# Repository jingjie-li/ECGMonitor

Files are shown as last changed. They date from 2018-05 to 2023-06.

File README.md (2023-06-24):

# Overview
This is a ECG/SPO2 Monitor Project. We mainly used TI's (Texas Instrument) [ADS1293](http://www.ti.com/product/ads1293)/[AFE4400](http://www.ti.com/product/AFE4400/description) analog front-end IC to acquire physiology data form human body, and used TI's [MSP430F149 MCU](http://www.ti.com/product/MSP430F149/description) to control these Chips, and send the data to our Android Smartphone App via TI's Bluetooth IC [CC2540](http://www.ti.com/product/CC2540/description). In our smartphone App, we can display ECG/PPG wavefore, compute & display SPO2,Heart Rate, and Heart Rate Variability(HRV), and control the hardware to running on different acquision mode (such as 3-Leads or 5-Leads mode).

To do so, we disigned and made a custome PCB using Autodesk EAGLE, did embedded system programing for MSP430 using IAR IDE, and some stuff about smartphone APP. We also had a 3D printed case for our circuit.

The major advantages of our system, is our outstanding power consumption performance. Our hardware only took about 300mW Power for Li-ion battery (about ~180mW for bluetooth). Also, our PCB is super portable, size less than 10-by-10cm.

We Shared the majority of our code and design files. Including MSP430 program, PCB layout, 3D printing models, and some APP code.

We do these stuff is for a [National BME(Biomedical Engineering) Competition for College Students](http://bmedesign.medmeeting.org/cn) in ShenZhen, China.

__On Aug 28, 2018: We just won the FIRST PRIZE in [National BME(Biomedical Engineering) Competition for College Students](http://bmedesign.medmeeting.org/cn) in ShenZhen, China. Which is the HIGHEST AWARD.__

Our Trophy and Certification

__Fig 1 Our First Prize Trophy and Certification__

# Quick access of our sub-modules
+ [Main MCU Controling Code](https://github.com/celelion/ECGMonitor/blob/master/MSP430/AFE%26ADS_inter/main.c)
+ [PCB Layout](https://github.com/celelion/ECGMonitor/tree/master/PCB)
+ [APP](https://github.com/celelion/ECGMonitor/tree/master/APP_Design)
+ [3D Printed PCB Case](https://github.com/celelion/ECGMonitor/tree/master/Case)
+ [Processing Tools for Computer Debugging](https://github.com/celelion/ECGMonitor/tree/master/Analog_Front/EEGPPGdataRecTest)
+ [Arduino DUE based IC chip(ADS1293/AFE4400) SPI interface verification code](https://github.com/celelion/ECGMonitor/tree/master/Analog_Front/Arduino-TestFirmware)

# Features
## Characteristics and Technical Indexes
### ECG

+ Differential Input Voltage Range: -400 mV ~ +400 mV
+ Common-Mode Rejection Ratio(CMRR): >100 dB
+ Differential Input Resistance: 500 MΩ
+ Sampling Rate: 150 Hz

### Oximeter
+ Sampling Rate: 50 Hz

### Power Consumption
| Overall Power | Bluetooth | ADS-ECG Module | AFE-Oximeter Module | MSP430-MCU Module |
| ------ | ------ | ------ | ------ | ------ |
| 291.1103 mW | 177.7327 mW | 3.1984 mW | 93.0931 mW | 17.0861 mW |

# Development Team
+ Jingjie Li (jingjie.li.21@ucl.ac.uk) - Hardware, PCB Layout, Part of MSP430 Programming, Debugging tools using Processing IDE, 3D modeling for the case
+ Jinming Li (lijinmingli@foxmail.com) - MSP430 Programming, Testing
+ Haoyi Tao - Android APP Programming

We are all class of 2019 BME undergraduate student from Xi'an Jiaotong University

# Hardware (By Jingjie Li)

Hardware

__Fig 2 The PCB layout of ECG/SPO2 Monitor Hardware__

We had a MainBoard, which contains mainly 5 modules, which is 
+ LDO Module for power supply; 
+ ADS Module for ECG; 
+ AFE Module for SPO2; 
+ MCU Module for controlling ;
+ Debugging module, for downloading program(BSL), Serial-USB conversion for a convenient debuging on PC using Processing IDE.

Parts

__Fig 3 Different parts and modules on our Main PCB__

## Power Tree

We used 4.8V Li-ion Battery or 5V USB to powering the whole system. 5V/4.8V is directly feed to USB chip CH340, and the Bluetooth Module. A TI LM1117 LDO chip proveide 3.3V power to ADS1293 ECG Module, and MSP430 MCU Module. 

PowerTree

__Fig 4 The Power Tree of our MainPCB__

Powering AFE4400 is a little bit more complicated, to give AFE4400 IC a much more stable voltage supply, we used a Ultra-Low-Noise, High-PSRR [TI TPS7A49](http://www.ti.com/product/TPS7A49/description) chip to provide 3V power for the AFE4400's digital supply (DIG SUP) pins. Then, we used a Low Noise 'Ceramic Stable' LDO [TI LP3878](http://www.ti.com/product/LP3878-ADJ/samplebuy) to provide 3.7v power for AFE4400 LED drive power supply pins (LED DRV). Using two chips, provided us a better isolation in AFE4400, which could minimize the voltage fluctuation interfere from ADS, MCU or AFE LED DRV parts.

## Connectors

For a common use, we choosed standard connectors and cables in our hardware design.

Hardware connection

__Fig 5 Hardware Connectors__

For example, for ECG, we used Mindray Standard 6-Pins, 5-Leads ECG cables and connectors; For SPO2, we used the standrad DB9 SPO2 Probe connector. So, it will be easy for our users to find new replcement when old probe is damaged.

## Signal Flow in our PCB

SignalFlow

__Fig 6 Signal Flow in our PCB__

In our hardware, we used MSP430 MCU to drive the SPI Bus (as a master device) to configrate ECG and SPO2 Chips (Write data on specific address), and read digital data form each chip.

The MSP430 MCU then compress, encode the sampled data to a long int, and send to the Bluetooth module (To smartphone APP) or a serial-USB debug module via UART.

MSP430 MCU also controled several indicator LED, which we could visulize the sampling rhythm (By flashing of the ADS/AFE LED). LEDs can also provided alarms such as ECG Lead off, SPO2 Cable off for us.

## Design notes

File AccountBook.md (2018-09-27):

# ECGMonitor
Account Book
 
Funding ~ 4500CNY

# Work

| Name        | Items    |  Money  | Amount| Parts| Fapiao Price
| --------   | :-----:   | :----: |  :----: | :----:|:----:|
Li,Jingjie | ECG Leads  |88 | 1| 2| 0
Li,Jingjie | Reflective Blood Sensor |30| 1 | 2 | 0
Li,Jinming | ADS1293 Test PCB | 74 | 5| 1| 74
Tao, Haoyi | ADS-TEST-Compount-Stuffs | 282 |~ | ~ | 985
Tao, Haoyi | Taxi 1 | 13.1|~|~|13.1
Li, Jingjie | Taxi 2 | 9.3 |~|~|9.3
Li,Jinming | Express fee of blueteeth | 5|1|1|0
Li,Jingjie | ADS-AFE Joint Test PCB | 123|5|1|123
Tao, Haoyi | PCB | 55 |~ | ~ | 100
Li,Jinming | Blueteeth | 15|4|1|60
Li,Jinming | DS-100A SPO2 |76|1|1|0
Li,Jinming | poster |40|1|1|0
Li,Jinming | PCB welding fee |250|1|1|0
Li,Jinming | electronic components |20|1|1|0
Li,Jinming | brochure |50|20|1|0
Li,Jinming | ECG Leads |63|1|1|0
Li,Jinming | DS-100A SPO2 |76|1|1|0
Li,Jinming | ECG PIN |38|1|1|0
Li,Jinming | ADS1293 QFN28 |174|4|4|0
Li,Jinming | Express fee of phone |19|1|1|19
Li,Jinming | battery |60|4|4|0
Li,Jinming | electrode slice |114|4|4|0

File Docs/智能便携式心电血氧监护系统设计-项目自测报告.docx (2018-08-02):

智能便携式心电血氧监护系统设计-项目自测报告说明

西安交通大学 仓鼠队 李金铭 李竞捷 陶豪毅

一、概述

本文档是对多生理信号数据采集与参数计算的监测系统设计（模拟前端由商品大规模集成专用电路实现）的功能和性能的测试。通过Netech公司的MINISIM 1000测试ECG信号和心率，通过biopac和本监测系统同时测试同一被试，测试Spo2信号。同时使用自主编写APP进行最终测试，包括滤波算法、波形显示等功能。

二、项目预期应用及标准基本要求概述

本设备预期可以用于心电图的显示，心率的监测和Spo2的监测。

项目基本要求是：

（1）可以正常显示心电、和PPG信号波形图；

（2）在一定范围内测得的心率基本正确；

（3）在一定范围内测得的Spo2值的误差在较小的范围内。

（4）功耗等性能

三、项目功能测试方案

1、 ECG、心率

测试设备：Netech公司的MINISIM 1000

测试步骤：

（1） 用MINISIM 1000产生幅值为1mV，30~210 bpm 不同心率的心电信号；
（2） 直接通过标准心电导联采集被试人心电；
（3） 用本监测系统测试信号，画出波形，计算心率。
2、 Spo2信号

测试设备：biopac

测试步骤：

（1） 用biopac和本监测系统同时测试同一人的血氧信号，被试通过憋气和深呼吸，分别获得91%~99%的血氧信号；
（2） 用本监测系统的结果进行拟合。

四、项目性能测试方案

1、心率检测精度

测试设备：Netech公司的MINISIM 1000

测试步骤：

（1） 用MINISIM 1000产生幅值为1mV，30~210 bpm 不同心率的心电信号；
（2） 采集不同心率信号2~3分钟并通过APP计算并显示心率；
（3） 计算误差及准确度

2、滤波性能

测试设备：APP

测试步骤：

（1） 采集人体心电信号并显示
（2） 设置正确滤波器参数并观察滤波后波形

3、血氧饱和度

测试设备：biopac

测试步骤：

（1） 利用样机和biopac同时采集被试血氧饱和度数据

（2） 被试进行憋气实验

（3） 观察两个设备Spo2值变化

4、 整体功耗性能测试：

测试设备：电流档位的电流表

测试步骤：

（1） 断开5V总电源处跳线，串入电流表，观察工作状态和待命状态电流，连接跳线，测量该处电压。
（2） 断开CH340串口模块跳线，从5V总电源处观察电压电流变化。
（3） 断开AFE血氧模块电源跳线，从5V总电源处观察电压电流变化。
（4） 在分立的心电模块的3.3V电源跳线处测量心电模块电压与电流。

五、项目功能与性能测试记录

（包含数据记录与图片等）

5.1 功能测试记录

1、心电及心率检测

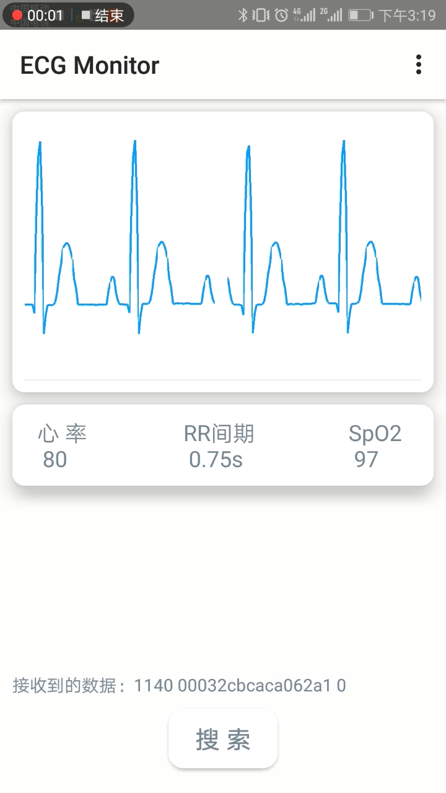
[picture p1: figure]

2、血氧饱和度检测

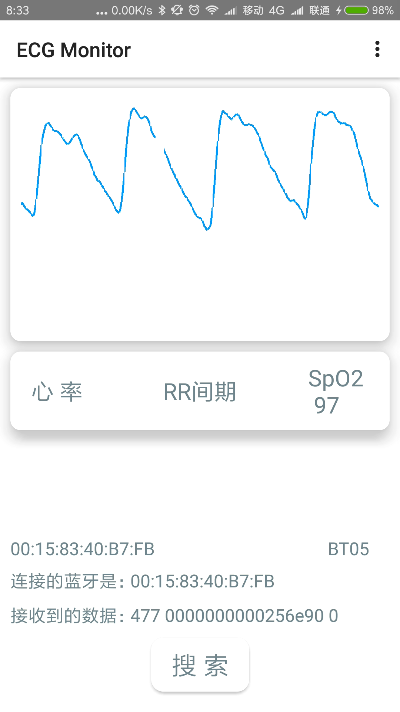
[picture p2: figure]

5.2 性能测试记录

1、ECG、心率检测

心率检测误差：

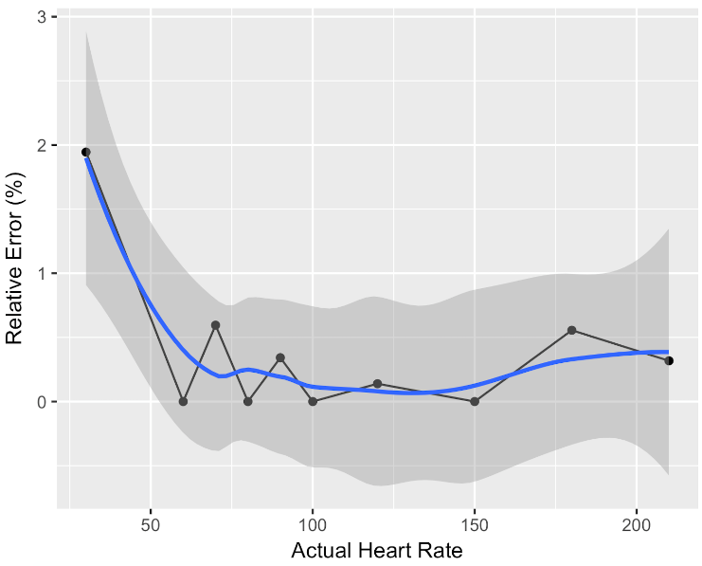
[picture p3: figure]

横轴为实际心率，纵轴为计算心率的相对误差

经过比较，相对误差小于2%

心电信号滤波：

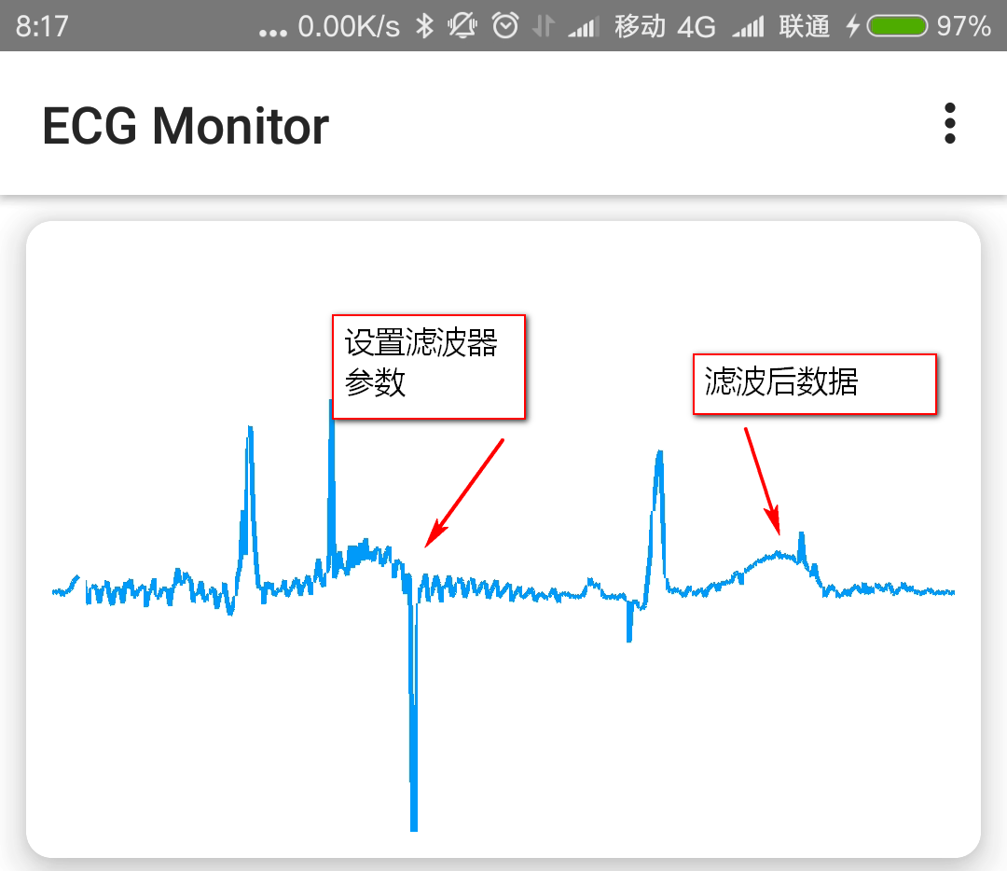
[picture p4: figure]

50Hz陷波器设置参数需要采样率，此处将采样率从默认200Hz调整为实际采样率225Hz，经一段时间后陷波器正常工作，去除50Hz干扰。

2、血氧饱和度动态监测：

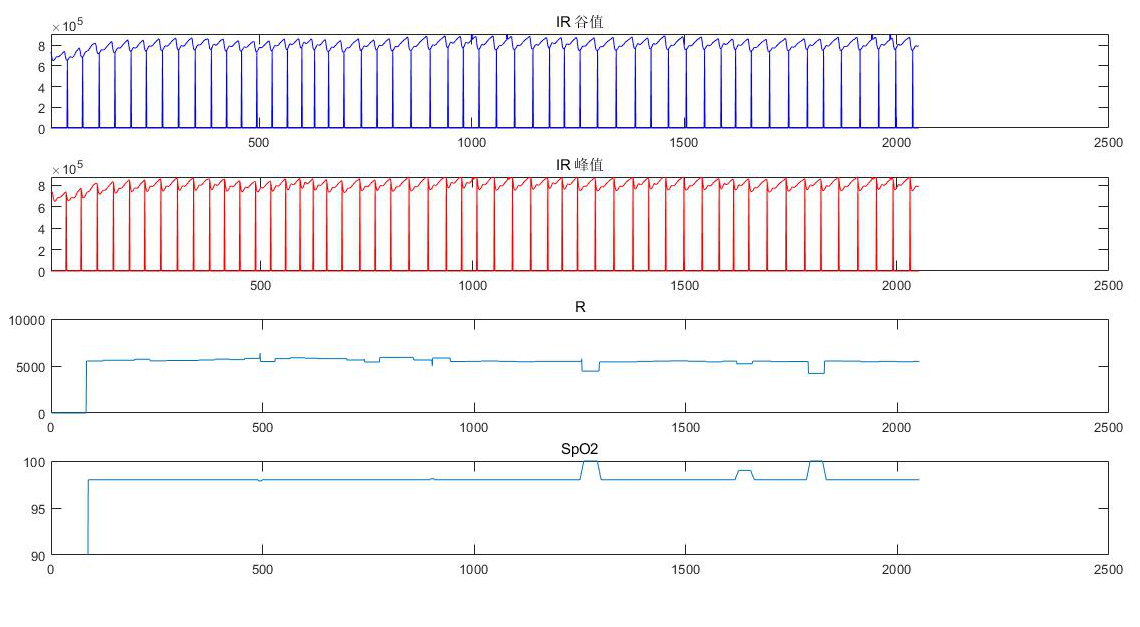
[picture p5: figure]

SpO2 经定标后经验公式为108-16.7*R( )

3、 心电信号输入范围：

可以实现0.15~5mV的检测

5.3 功耗测试记录如下：

1、整体工作和静息功耗

| 工作 | 静息
电压 | 5.08v | 5.07v
电流 | 1.05mA | 0.41mA
功耗 | 5.334mW | 2.0708mW

2.去除USB串口芯片后 静息状态电流为0.29mA，电压为5.07v，总功耗大约为1.4703mW。

3.去除AFE芯片电源跳线后，静息状态电流为0.28mA，电压为5.12v，总功耗大约为1.4336mW。

4. ADS模块工作时电压为3.289V，0.373mA，功耗为1.2268mW。

5.去除蓝牙模块后，电压为5.12V，电流为0.97mA，功耗为4.9664mW。

6.在去除USB芯片、蓝牙模块的基础商，电压电流分别为：0.69mA，5.08V，功耗为3.5052mW去除单片机，电压为5.14v，电流为0.67mA，功耗为3.4438mW。因此MSP430单片机模块产生功率。采集时，由于MSP仍然可以通过串口电压工作，无法从串联的电流表获取电压，因此无法测到其功耗。

模块 | 蓝牙 | 单片机 | 心电 | 血氧 | USB
功耗 | 0.3676mW | 0.0614mW(等待) | 1.2268mW | 3.9004 | 0.6005mW

六、小结

本项目目前可以较好的做到波形自适应显示及50hz陷波，在心电数据及心率较为合适的情况下可以准确检测出心率，当心率过低或过高时会发生一定误差，需要进一步优化；血氧饱和度计算经拟合经验公式后可以较为准确得出，误差不超过2%。

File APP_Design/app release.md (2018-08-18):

## V1.0.1

- 修复几个小bug
- 更换了侧边栏 ```Header``` 背景图
- 点击侧边栏 ```Header``` 处 “个人信息” 即可进入 “设置” 页面 

## V1.0.0

- 第一代完整版 ```App```
- 添加有 ```使用说明```、```设置```、```反馈```、```关于``` 等页面
- 首页仅 ```主菜单按钮```，便捷化操作
- 波形操作功能完善，有 ```绘制、重置、缩放、上下平移、陷波器选择、波形自适应选择``` 等

## V0.9.0

- 雏形版，功能不完善

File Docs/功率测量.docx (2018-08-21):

实测功率

| 总功率 | ADS+MCU功率 | AFE功率
待机模式 | 107.2741 mW | 17.7225 mW | 0.1001 mW
正常模式 | 291.1103 mW | 23.5593 mW | 93.0931 mW
仅心电模式 | 116.1548 mW | 20.2845 mW | 0.0064 mW
仅血氧模式 | 289.4695 mW | 20.3609 mW | 95.7865 mW

分析功率

| 总功率 | 蓝牙模块 | ADS模块 | AFE模块 | MCU模块
功率 | 291.1103mW | 177.7327mW | 3.1984mW | 93.0931mW | 17.0861mW

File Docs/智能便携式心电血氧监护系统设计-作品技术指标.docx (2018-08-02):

智能便携式心电血氧监护系统设计-作品技术指标

西安交通大学 仓鼠队 李金铭 李竞捷 陶豪毅

一、概述

多生理信号数据采集与参数计算的监测系统（模拟前端由商品大规模集成专用电路实现）可以实现很方便的对心电、心率和血氧信号的监测。本文档是对其技术指标的描述，具体包括心电的准确度、心率的准确度、血氧的准确度、滤波算法和波形显示等

二、项目预期应用及相关标准基本要求

本设备预期可以用于心电图的显示，心率的监测和Spo2的监测。

项目基本要求是：

（1）可以正常显示心电和PPG信号波形图；

（2）在一定范围内测得的心率基本正确；

（3）在一定范围内测得的Spo2值的误差在较小的范围内。

（4）功耗较低。

三、项目预期功能

（1）可以在APP上实时显示心电波形图，波形图可以明显看出P波、QRS波和T波。

（2）在30~200 bpm心率范围内可以准确计算并显示心率

（3）可以在APP上实时显示PPG波形

（4）在85%~100%的血氧饱和度范围内，可以准确地计算出Spo2

（5）在导联脱落的时候会发生报警

四、项目预期性能

（1）在30~200 bpm心率范围内，心率计算误差不超过±2bpm；

（2）在85%~100%的血氧饱和度范围内，Spo2计算误差不超过±2%；

（3）可以显示范围在0.15~5mV内的心电波形，波形可以自适应显示，达到最好人眼观测效果；

（4）实现心电波形的滤波；

（5）未来可以做到心电和PPG波形同时显示；

（6）幅值在1~5mV范围内时可以准确计算心率；

（7）功耗尽可能的小，便于使用电池进行长时间的使用

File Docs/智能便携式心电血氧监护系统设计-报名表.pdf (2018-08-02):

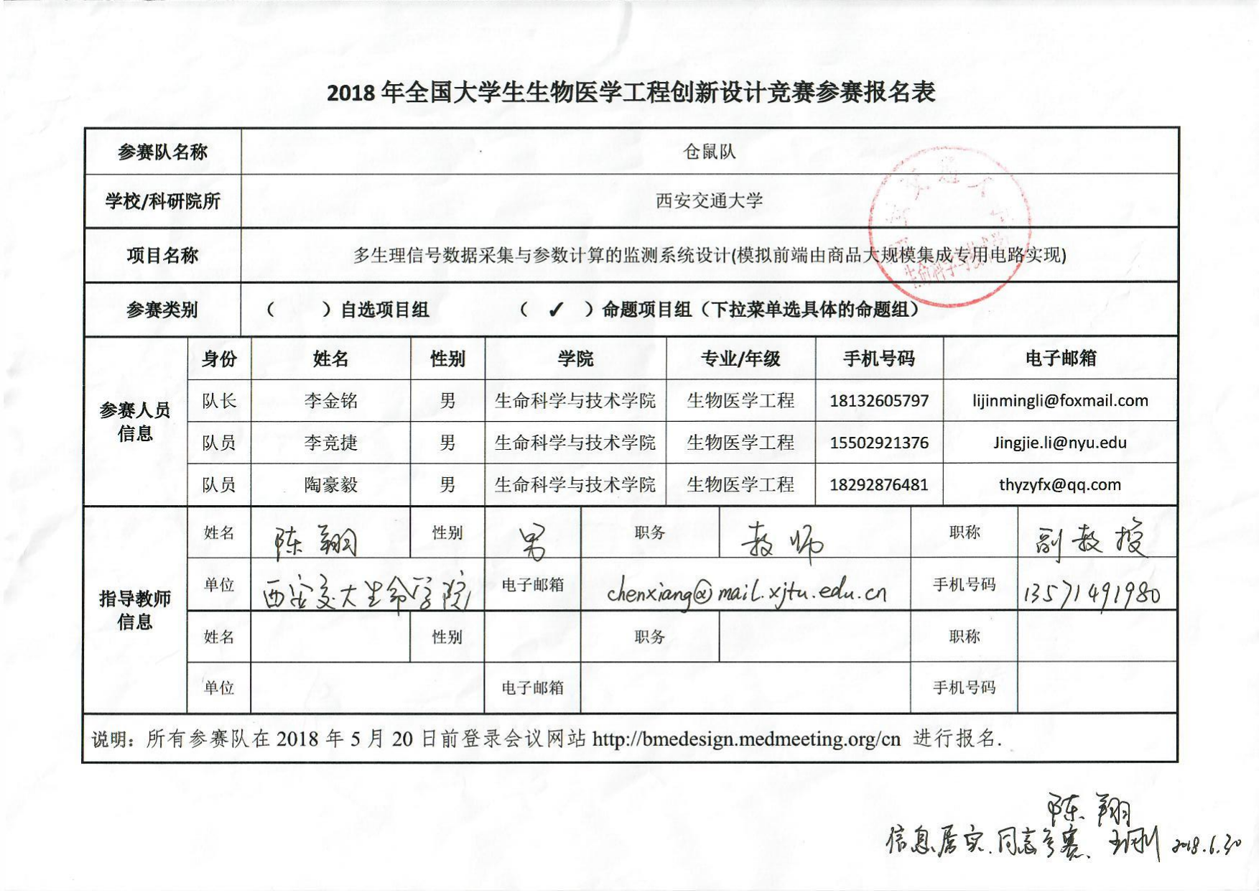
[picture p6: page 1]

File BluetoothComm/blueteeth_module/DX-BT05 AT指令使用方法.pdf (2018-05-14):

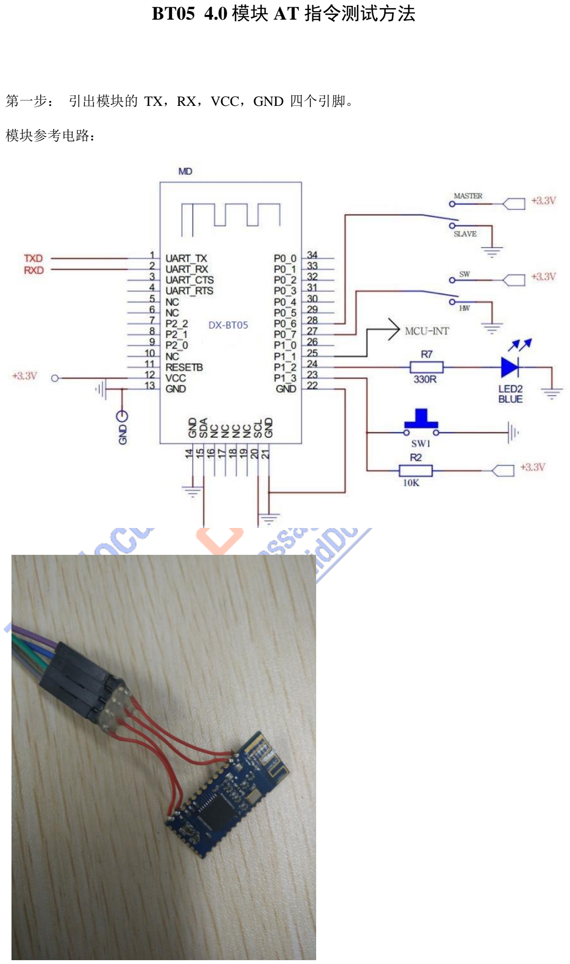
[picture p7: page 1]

### BT05 4.0 模块 AT 指令测试方法

第一步： 引出模块的 TX，RX，VCC，GND 四个引脚。

模块参考电路：

第二步：准备一个 USB 转串口

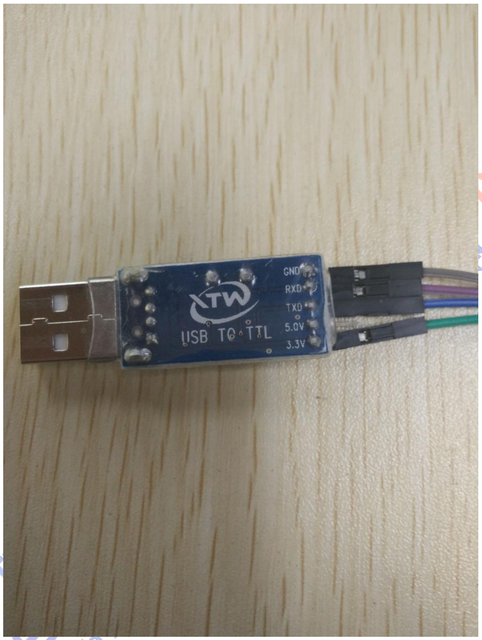
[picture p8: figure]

第三步：将模块和 USB 转串口的引脚连接好， 并插入到 PC 端的 USB 口上

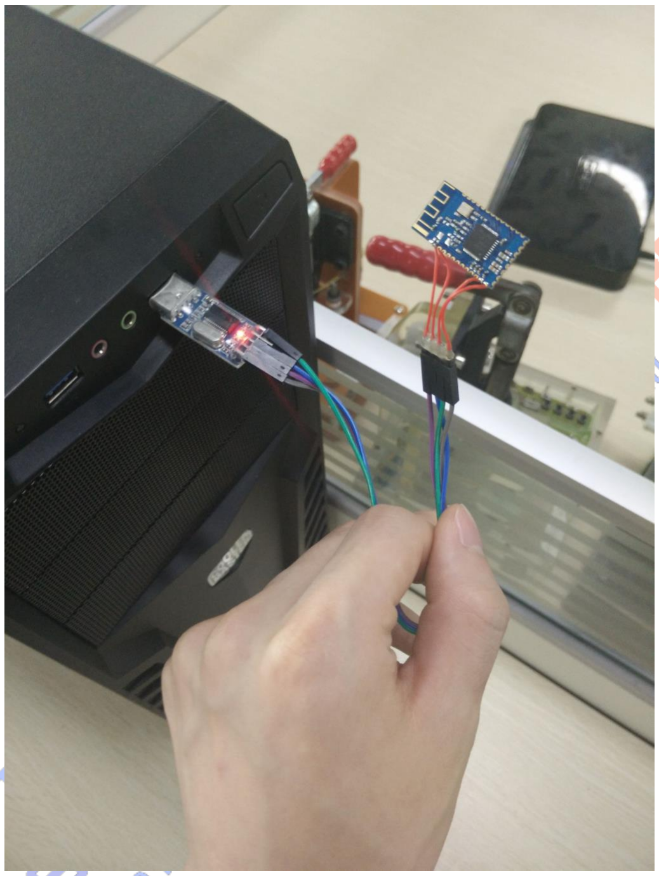
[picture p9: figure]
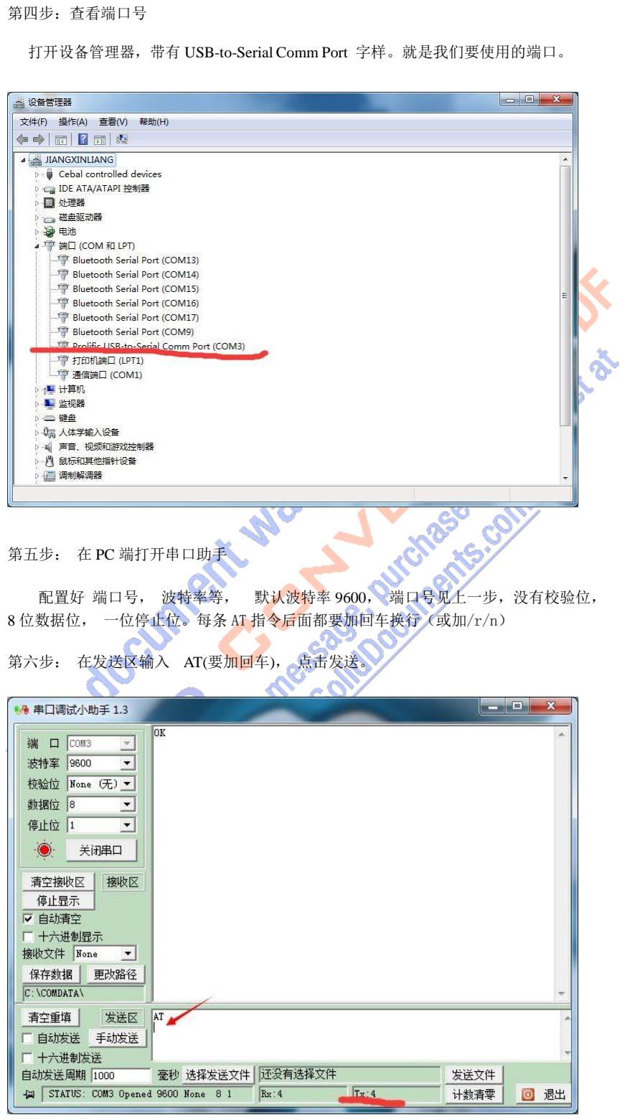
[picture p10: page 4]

第四步：查看端口号

打开设备管理器，带有 USB-to-Serial Comm Port 字样。就是我们要使用的端口。

第五步： 在 PC 端打开串口助手

配置好 端口号， 波特率等， 默认波特率 9600， 端口号见上一步，没有校验位， 8 位数据位， 一位停止位。每条 AT 指令后面都要加回车换行（或加/r/n）

第六步： 在发送区输入 AT(要加回车)， 点击发送。

在发送区输入 AT(要加回车)， 点击发送。

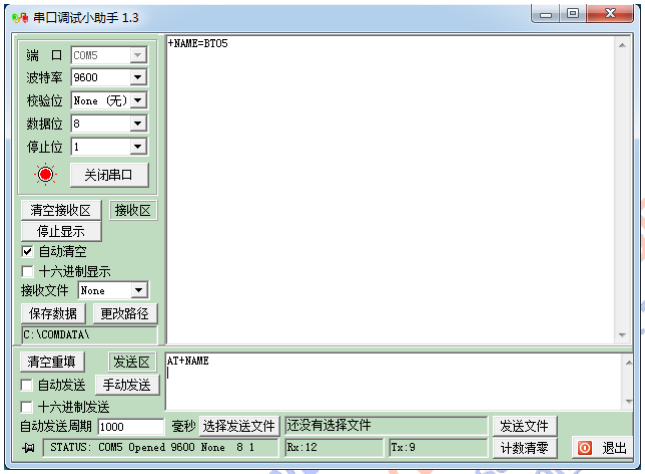
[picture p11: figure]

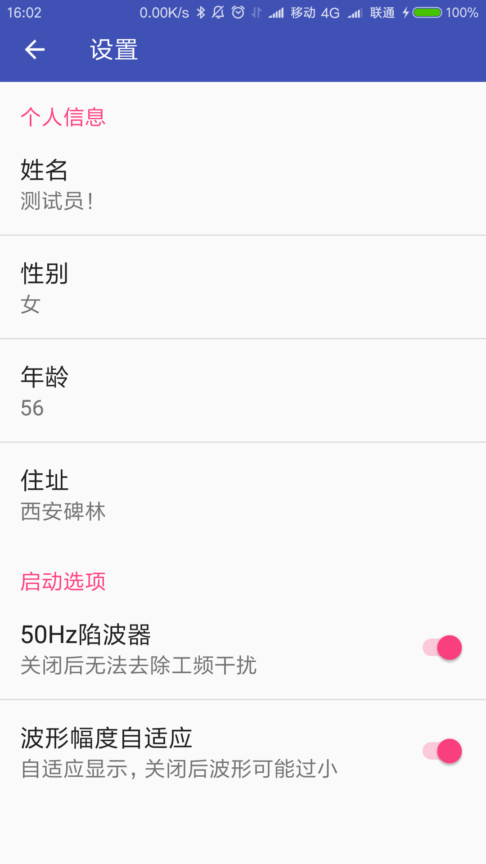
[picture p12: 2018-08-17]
APP_Design/V1.0.0_setting.png

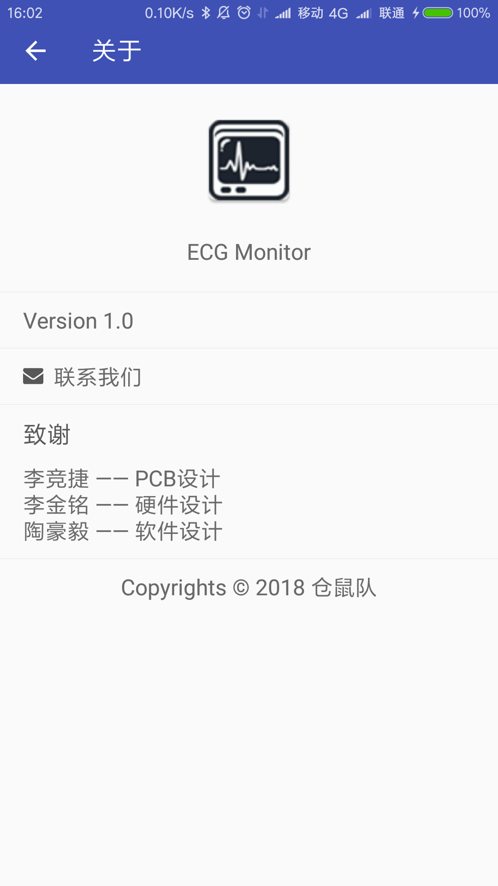
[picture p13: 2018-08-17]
APP_Design/V1.0.0_about.png

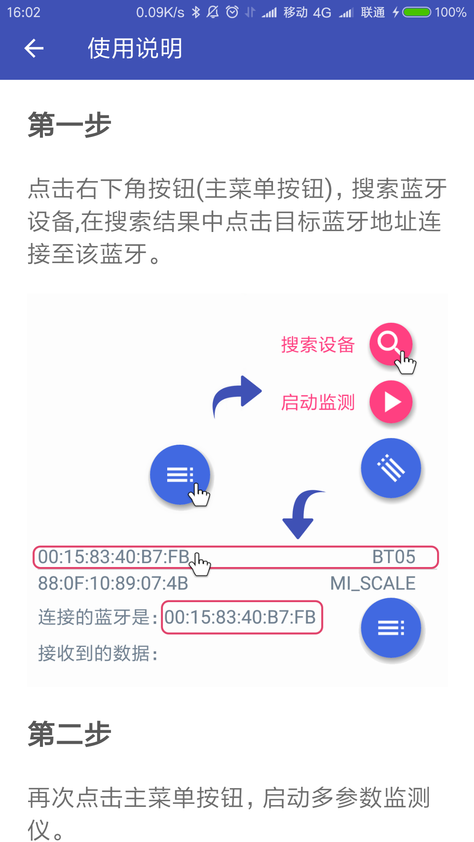
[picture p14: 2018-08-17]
APP_Design/V1.0.0_help.png

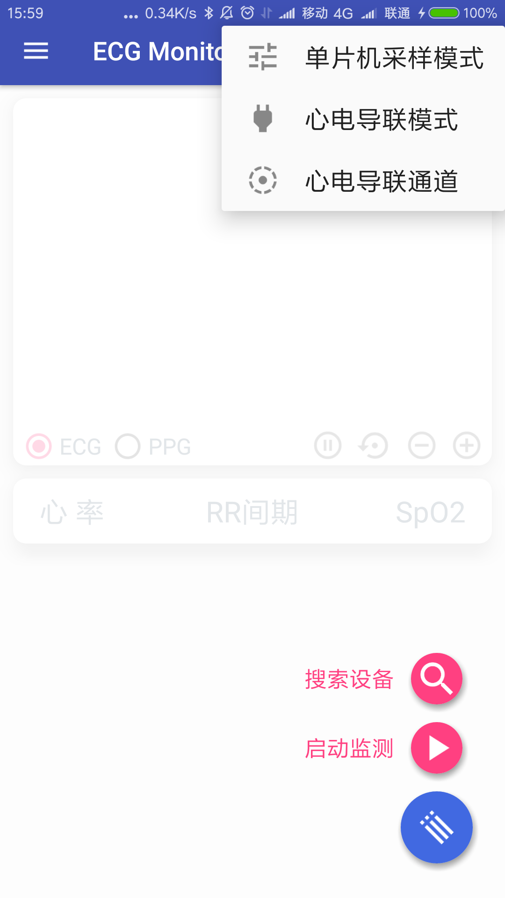
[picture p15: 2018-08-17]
APP_Design/V1.0.0_1.png

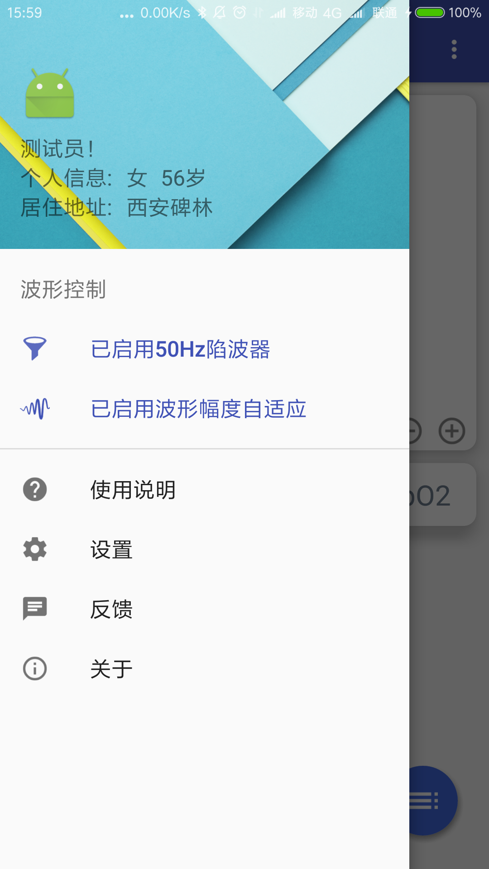
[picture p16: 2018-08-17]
APP_Design/V1.0.0_2.png

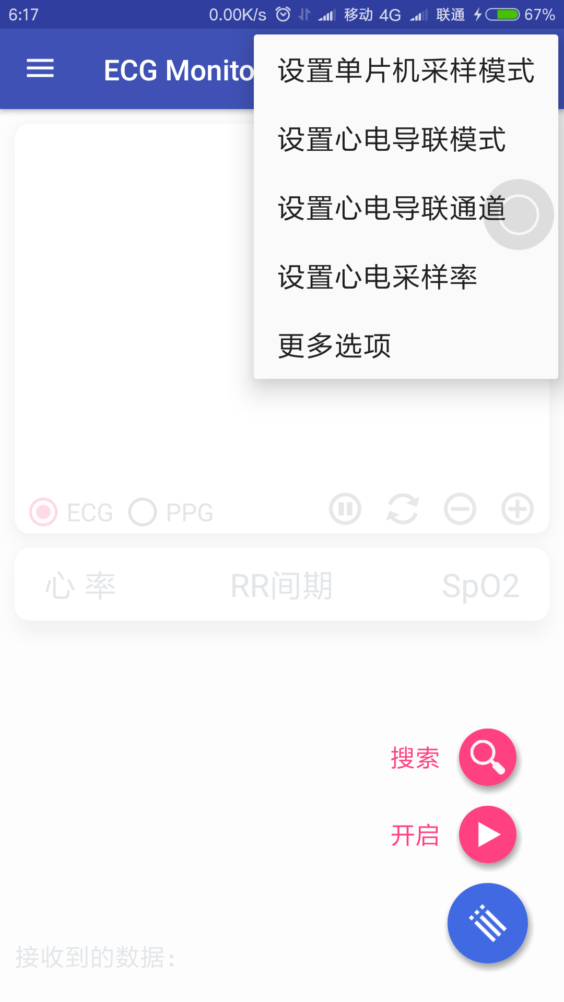
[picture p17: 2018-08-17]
APP_Design/app_v0.9.0.png

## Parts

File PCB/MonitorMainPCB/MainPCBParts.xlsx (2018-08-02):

心电-血氧监测系统元件列表
元件 | 位号 | 每片数量
贴片电容 0.1uF-0603 | C1,C4,C5,C6,C10,C11,C25,C29,C30,C34,C35,C38,C42 | 13
直插电容100uF | C2,C3 | 2
贴片电容1.0uF-0603 | C7,C26,C39 | 3
贴片电容22pF-0603 | C8,C9,C36,C37 | 4
贴片电容1nF-0603 | C12,C16 | 2
贴片电容10uF-1206 | C13,C17,C18,C19,C20,C22,C23,C24,C43 | 9
贴片电容10nF-0603 | C14,C15,C21,C27 | 4
贴片电容2.2uF-0603 | C28,C31 | 2
贴片电容-18pF-0603 | C32,C33 | 2
贴片电容-30pF-0603 | C40,C41 | 2
贴片LED-绿色-1206 | D1 | 1
贴片LED-红色-0603 | D5,D6,D7,D8,D9 | 6
贴片开关二极管-BAV99S-SOT363 | D2,D3 | 2
贴片电感 3.3uH/450mA-0805 | L1,L2,L3,L4 | 4
贴片电感 1uH/450mA-0805 | 无 | 4
贴片电阻0R-0603 | R1,R3,R10,R11,R12,R13,R14,R15,R16,R20,R21,R24,R25,R26,R27,R28,R30,R31,R32,R33,R34,R35,D4 | 21
贴片电阻1M欧-0603 | R2,R5,R6,R7 | 4
贴片电阻51欧-0603 | R4 | 2
贴片电阻10k欧-0603 | R8,R37,R46 | 3
贴片电阻10M欧-0603 | R9 | 1
贴片电阻2.55k欧-0603 | R17 | 1
贴片电阻1k欧-0603 | R18,R29,R50,R51,R52,R53,R54 | 7
贴片电阻4.7k欧-0603 | R19,R44 | 2
贴片电阻75k欧-0603 | R22 | 1
贴片电阻47k欧-0603 | R23 | 1
贴片电阻10欧-0603 | R36,R47,R48,R49 | 4
贴片电阻130欧-0603 | R38,R39,R40,R41,R42,R43 | 6
贴片电阻1欧-0603 | R45 | 1
直插晶震4.096MHz-HC49S封装 | Y1 | 1
贴片晶震8MHz-5X3.2-4脚 | Y2,Y5 | 2
贴片晶震12MHz-5X3.2-4脚 | Y3 | 1
贴片晶震32.768kHz-3.2X1.5MM | Y4 | 1
芯片MSP430F149IPAG，QFP50P1200X1200X120-64N封装 | U4 | 1
芯片AFE4400_RHA_40，RHA40_4P15X4P15封装 | IC2 | 1
芯片CH340G，SOIC16封装 | U5 | 1
芯片TPS7A4901DGNR，SOP65P490X110-9N封装 | U2 | 1
芯片LP3878MR-ADJ_NOPB，SOIC127P602X168-9N封装 | U3 | 1
芯片ADS1293，QFN28-5X5封装 | IC1 | 1
稳压芯片LM1117 3.3v，SOT223封装 | U1 | 1
DC电源插座5.5-2.1mm 直插 | J1 | 1
USB-B型 母座，直插 | J2 | 1
DB9母座，直插 | J3 | 1
2.54mm单排直插排针 | J4,J5 | 0
2.54mm双排排针 | J6 | 5
2.54mm长针单排母座 | J7 | 1
直插按键5mm*5mm*6 | S1,S2,S3 | 3

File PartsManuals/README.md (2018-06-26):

# ECGMonitor
Project

# Parts Mamuals Folder
For storing particular chip's manual/datasheet

# TI Solution Web-book
## ECG Monitor Solution
Link: [http://www.ti.com.cn/solution/cn/ecg_electrocardiogram](http://www.ti.com.cn/solution/cn/ecg_electrocardiogram)
### Important Parts
+ ADS1298 (Complex analog front, not going to use, too expensive)
+ ADS1293 (This stuff is what we are going to use)
+ MSP430FG439(Recommender), MSP430F149(easy to buy) 

# Manual List

## AFE4400 Integrated Analog Pulse Oximeters
datasheet: [AFE4400.pdf](https://github.com/celelion/ECGMonitor/blob/master/PartsManuals/AFE4400.pdf)

web:[TI Link](http://www.ti.com.cn/product/cn/afe4400)

buy:[DigiKey Link](https://www.digikey.com.cn/product-detail/zh/texas-instruments/AFE4400RHAR/296-38860-1-ND/5142978)

example:[TI](http://www.ti.com.cn/tool/cn/TIDA-00311)

PDF:[tidu542](https://github.com/celelion/ECGMonitor/blob/master/PartsManuals/tidu542.pdf)

## ADS1293 Analog front-end chip
datasheet: [ads1293.pdf](https://github.com/celelion/ECGMonitor/blob/master/PartsManuals/ads1293.pdf)

web:[TI Link](http://www.ti.com.cn/product/cn/ADS1293/technicaldocuments)

buylink:[digikey](https://www.digikey.com.cn/product-detail/zh/texas-instruments/ADS1293CISQE-NOPB/296-35511-1-ND/3768438)

example:[TI Link](http://www.ti.com.cn/tool/cn/TIDA-00096)

PDF:[tidu195a.pdf](https://github.com/celelion/ECGMonitor/blob/master/PartsManuals/tidu195a.pdf)

## ADS1298 Analog front-end chip
ADS-1298-Analog Front-End for Biopotential Measurement Chip.pdf
website:[TI Link](http://www.ti.com.cn/product/cn/ads1298)

## MSP430FG439

link:[http://www.ti.com.cn/product/cn/MSP430FG439/toolssoftware](http://www.ti.com.cn/product/cn/MSP430FG439/toolssoftware)

## MSP430F149

link:[http://www.ti.com.cn/product/cn/MSP430F149/technicaldocuments](http://www.ti.com.cn/product/cn/MSP430F149/technicaldocuments)

# About ADS1293 Ctrl Regs
AFE_RES(0x13h<0x00h)-> 102.4-kHz clock freq for ADC

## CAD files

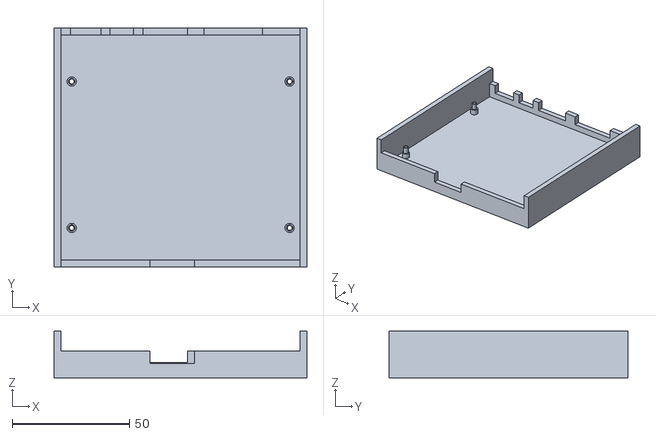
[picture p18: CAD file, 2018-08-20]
Case/ECGMCase_Base.stl
107.9 x 101.9 x 20.0

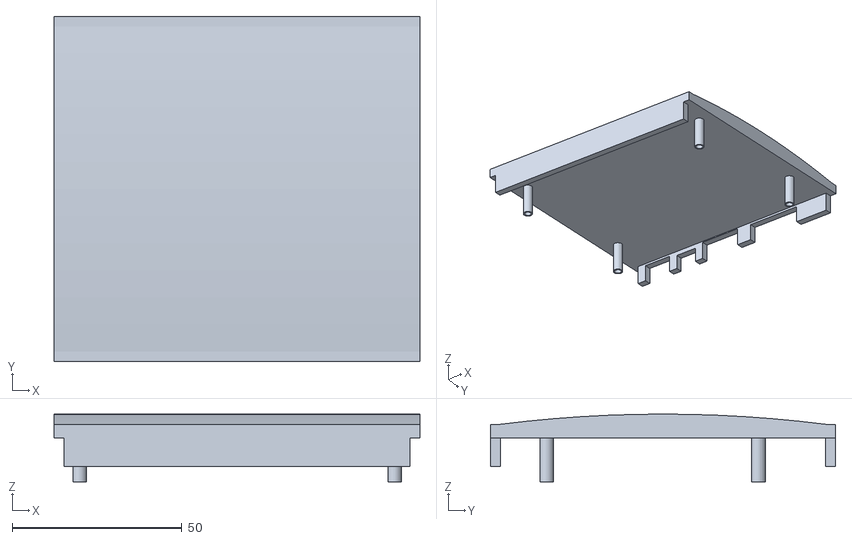
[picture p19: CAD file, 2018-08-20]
Case/ECGMCase_Upper.stl
107.9 x 101.9 x 20.0

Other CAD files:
Case/ECGMCase.skp
Case/ECGMCase_Base.skp
Case/ECGMCase_Upper.skp
Case/ECGMCase~.skp

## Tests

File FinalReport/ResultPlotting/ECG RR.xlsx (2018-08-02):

ActualHR | DetectedHR | Error
30 | 30 | 0
30 | 29 | 3.333333333
30 | 30 | 0
30 | 30 | 0
30 | 29 | 3.333333333
30 | 30 | 0
30 | 25 | 16.66666667
30 | 30 | 0
30 | 30 | 0
30 | 30 | 0
30 | 30 | 0
30 | 30 | 0
60 | 60 | 0
60 | 60 | 0
60 | 60 | 0
60 | 60 | 0
60 | 60 | 0
60 | 60 | 0
60 | 60 | 0
60 | 60 | 0
60 | 60 | 0
60 | 60 | 0
60 | 60 | 0
60 | 60 | 0
60 | 60 | 0
70 | 70 | 0
70 | 69 | 1.428571429
70 | 70 | 0
70 | 70 | 0
70 | 69 | 1.428571429
70 | 70 | 0
70 | 69 | 1.428571429
70 | 70 | 0
70 | 69 | 1.428571429
70 | 70 | 0
70 | 69 | 1.428571429
70 | 70 | 0
80 | 80 | 0
80 | 80 | 0
80 | 80 | 0
80 | 80 | 0
80 | 80 | 0
80 | 80 | 0
80 | 80 | 0
80 | 80 | 0
80 | 80 | 0
80 | 80 | 0
80 | 80 | 0
80 | 80 | 0
80 | 80 | 0
80 | 80 | 0
90 | 90 | 0
90 | 89 | 1.111111111
90 | 90 | 0
90 | 90 | 0
90 | 89 | 1.111111111
90 | 90 | 0
90 | 89 | 1.111111111
90 | 90 | 0
90 | 90 | 0
90 | 90 | 0
90 | 90 | 0
90 | 89 | 1.111111111
90 | 90 | 0
100 | 100 | 0
100 | 100 | 0
100 | 100 | 0
100 | 100 | 0
100 | 100 | 0
100 | 100 | 0
100 | 100 | 0
100 | 100 | 0
100 | 100 | 0
100 | 100 | 0
100 | 100 | 0
100 | 100 | 0
100 | 100 | 0
100 | 100 | 0
120 | 118 | 1.666666667
120 | 120 | 0
120 | 120 | 0
120 | 120 | 0
120 | 120 | 0
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

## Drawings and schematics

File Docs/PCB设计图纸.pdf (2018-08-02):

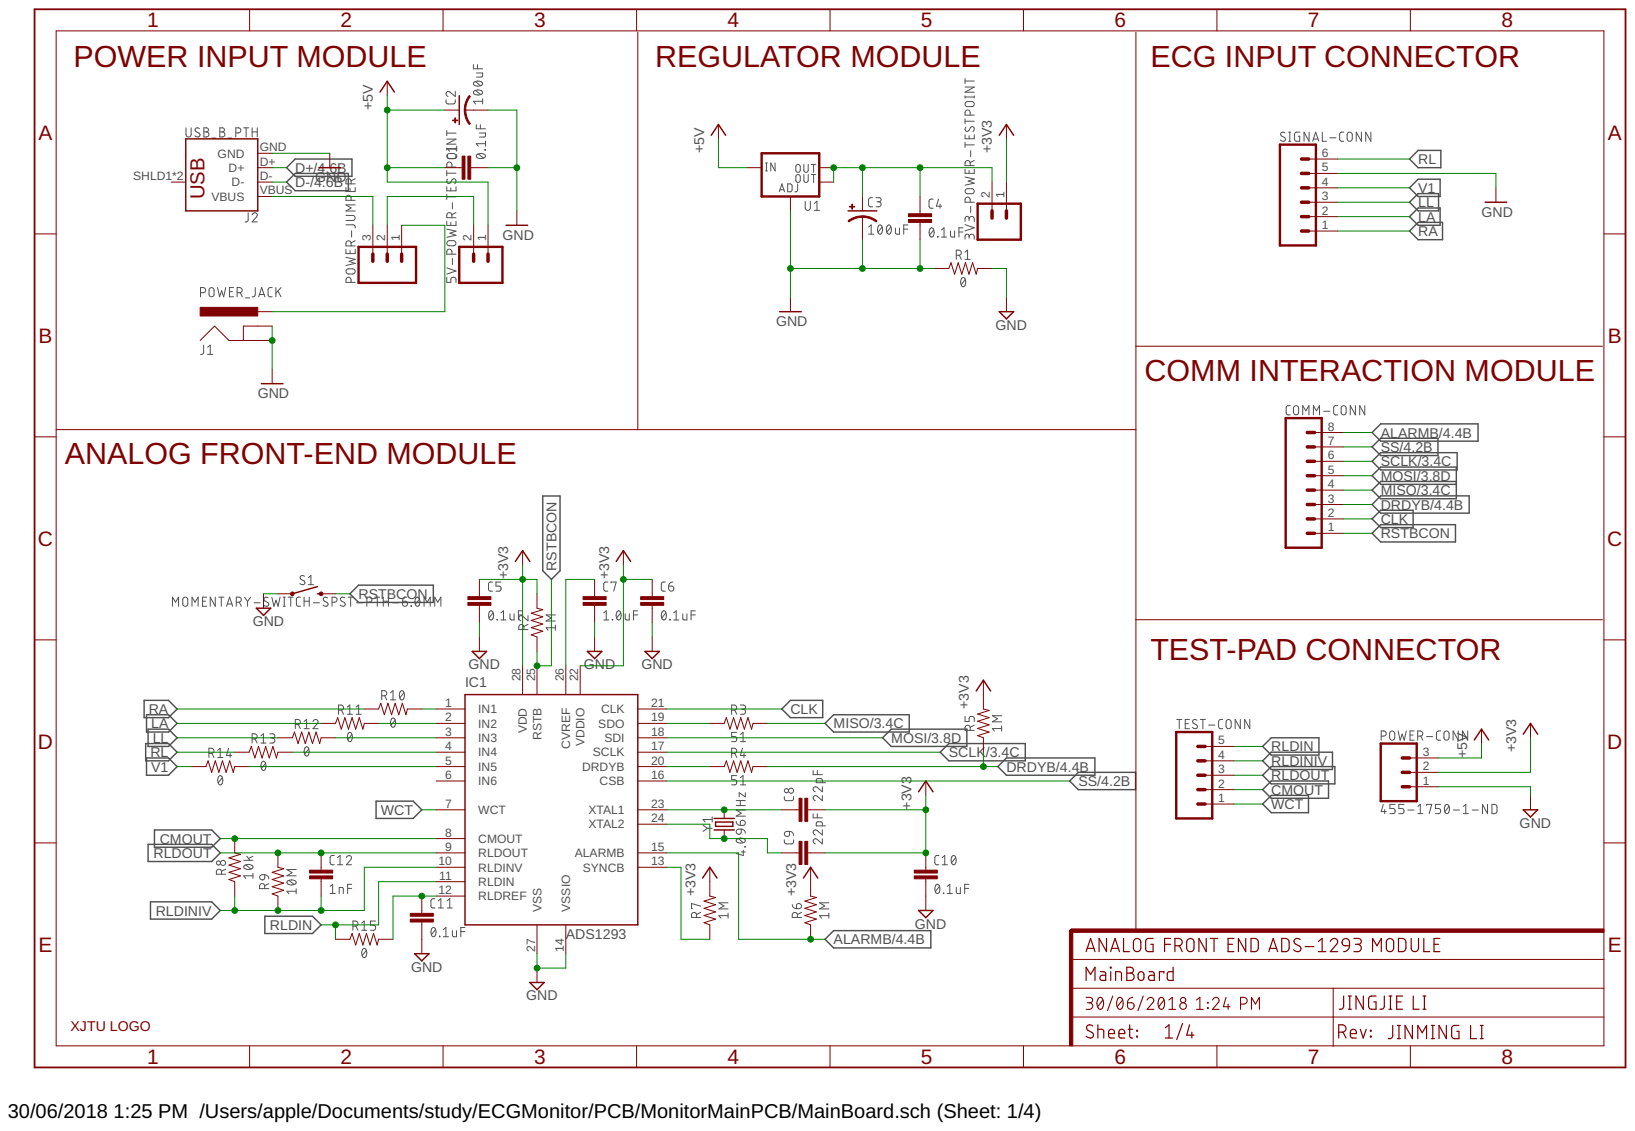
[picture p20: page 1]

ANALOG FRONT-END MODULE

TEST-PAD CONNECTOR | GND

RLDOUT 9
RLDINV 10
RLDIN 11
RLDREF 12

30/06/2018 1:25 PM /Users/apple/Documents/study/ECGMonitor/PCB/MonitorMainPCB/MainBoard.sch (Sheet: 1/4)

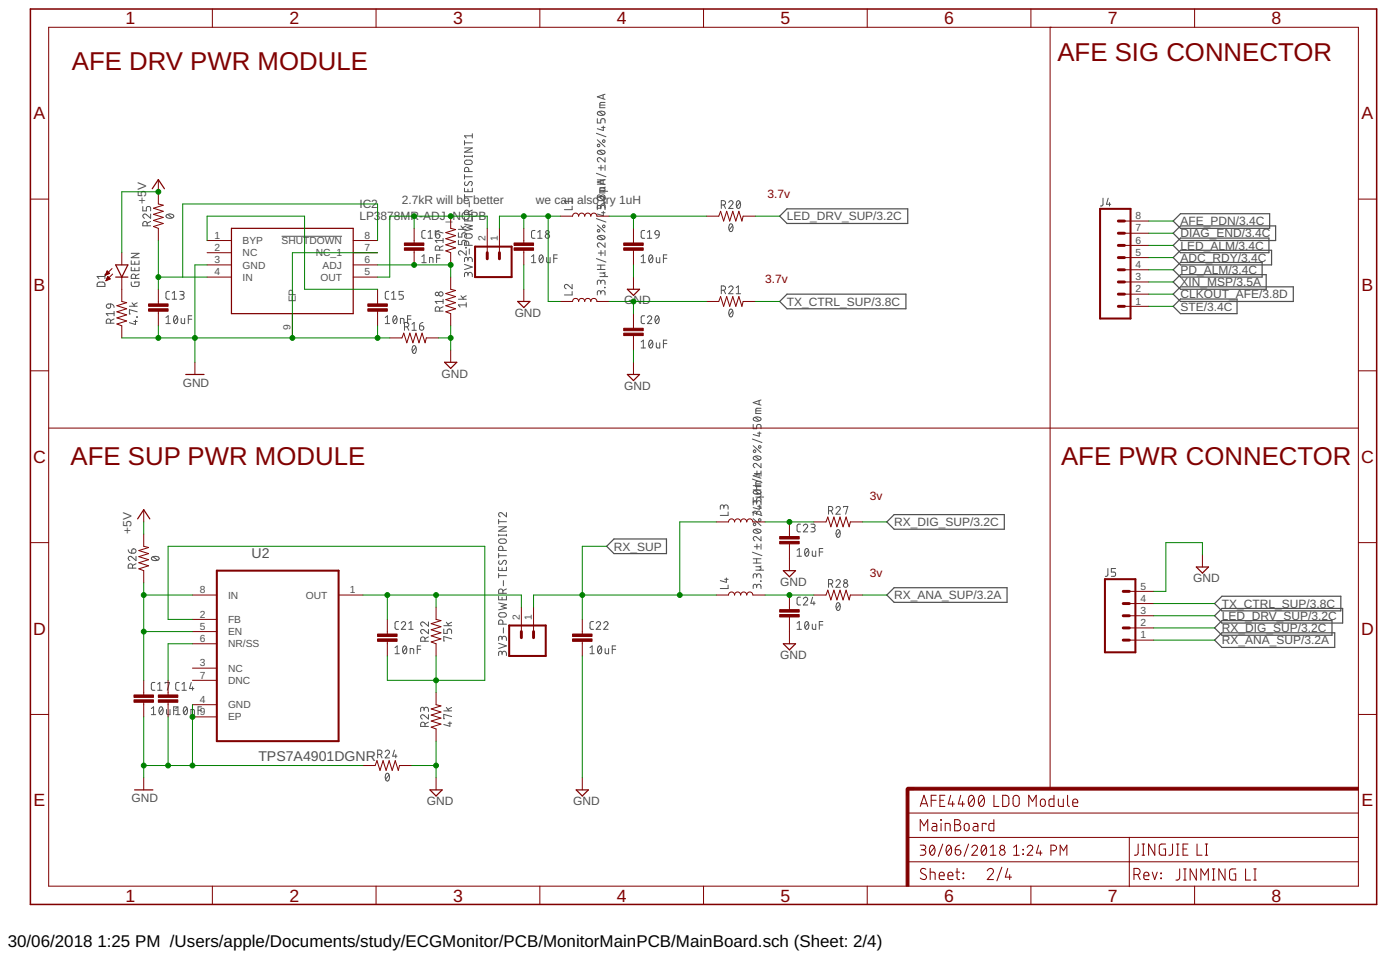
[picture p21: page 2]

AFE SUP PWR MODULE | AFE PWR CONNECTOR

30/06/2018 1:25 PM /Users/apple/Documents/study/ECGMonitor/PCB/MonitorMainPCB/MainBoard.sch (Sheet: 2/4)

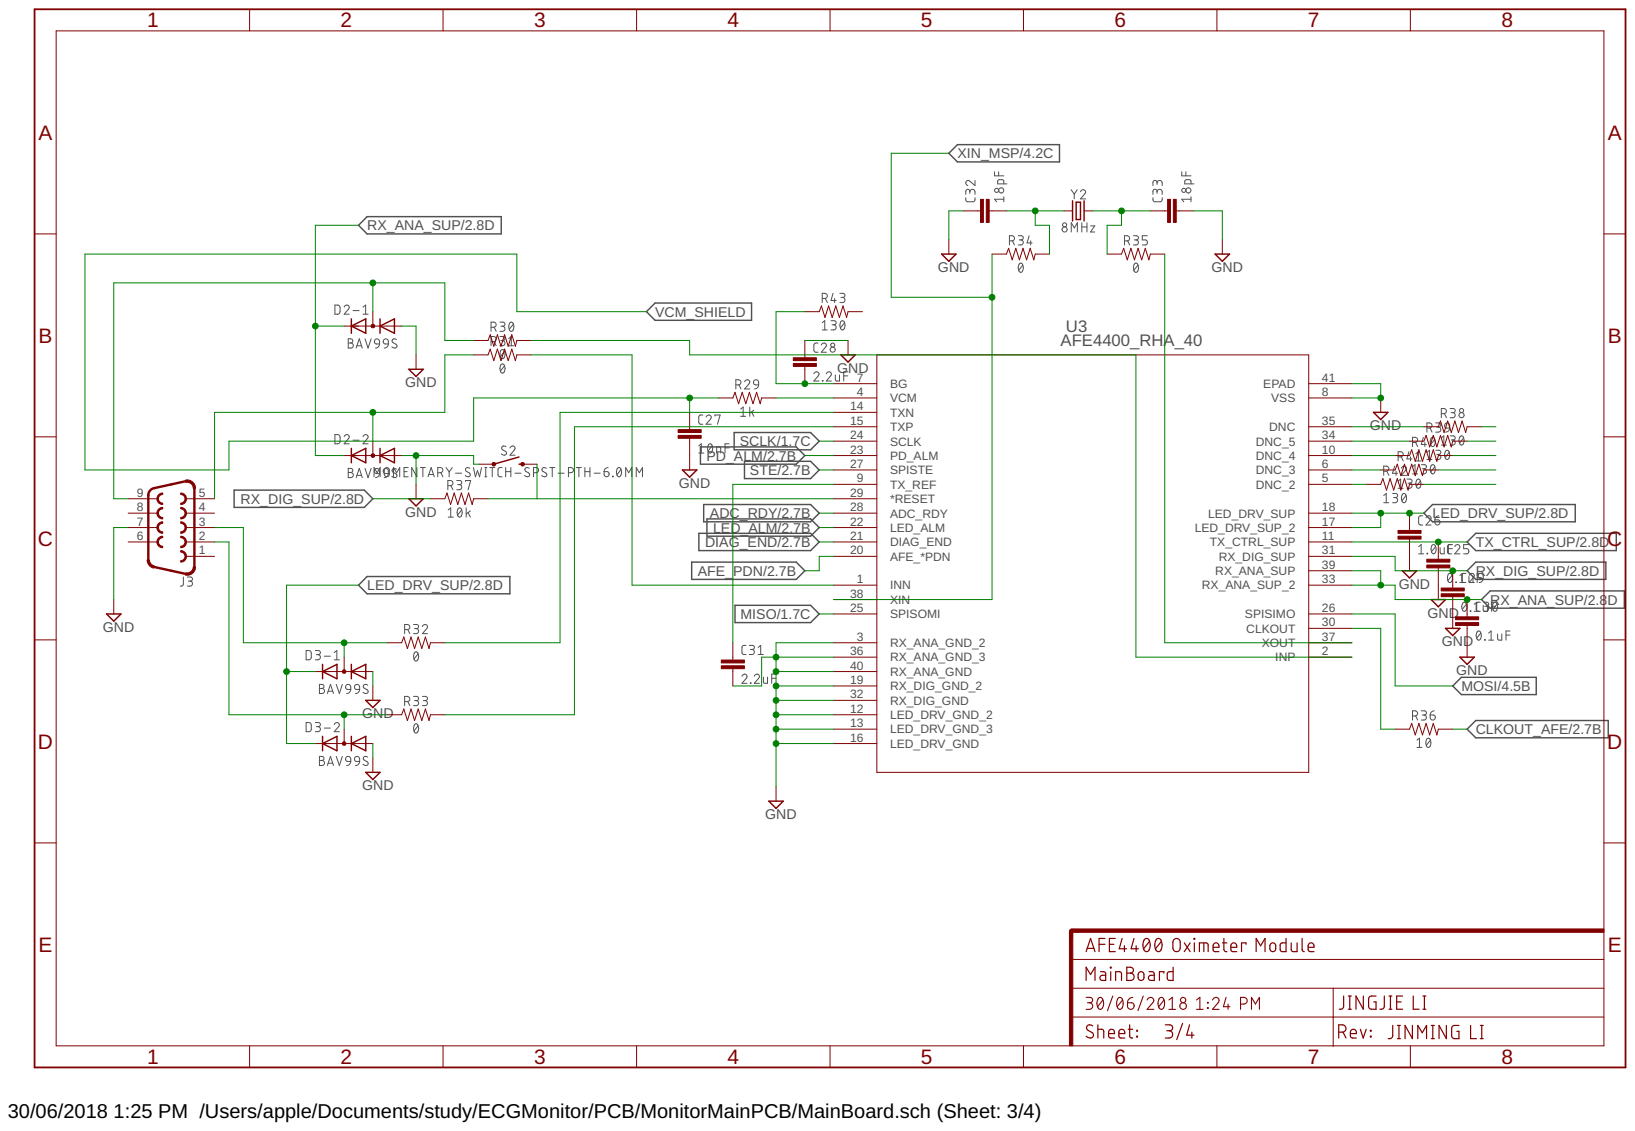
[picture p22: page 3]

30/06/2018 1:25 PM /Users/apple/Documents/study/ECGMonitor/PCB/MonitorMainPCB/MainBoard.sch (Sheet: 3/4)

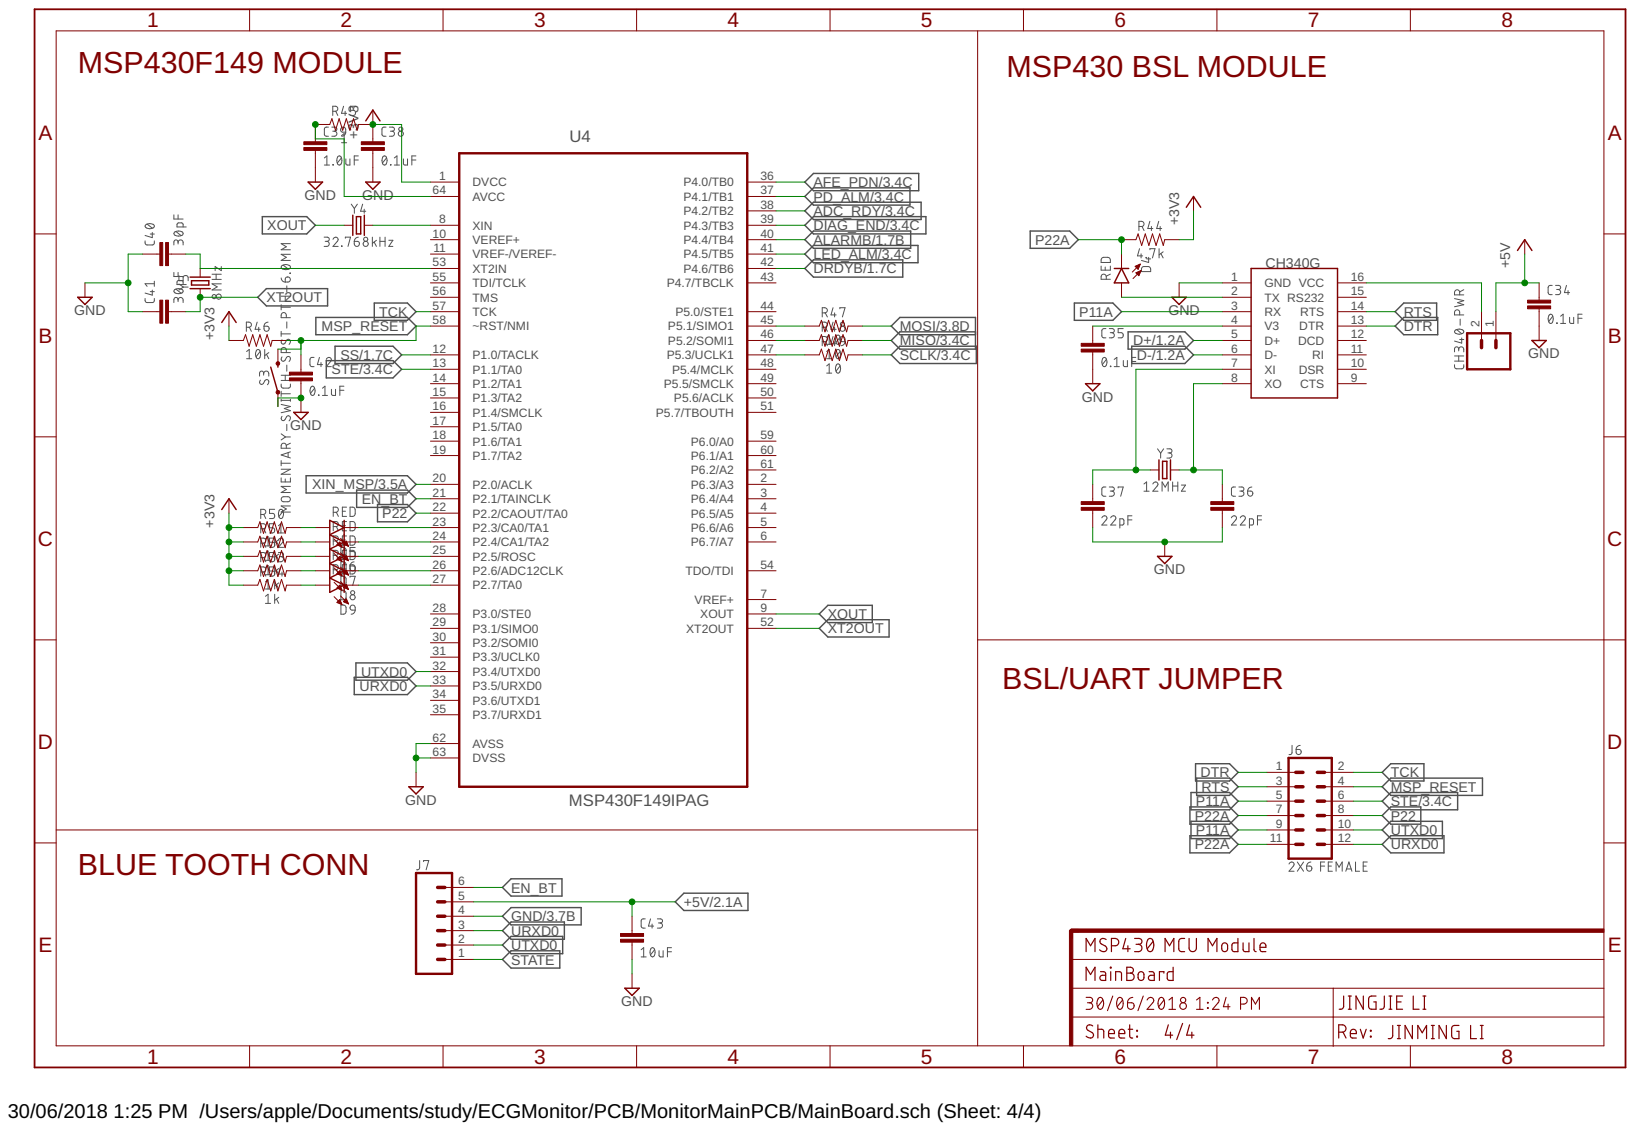
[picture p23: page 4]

30/06/2018 1:25 PM /Users/apple/Documents/study/ECGMonitor/PCB/MonitorMainPCB/MainBoard.sch (Sheet: 4/4)

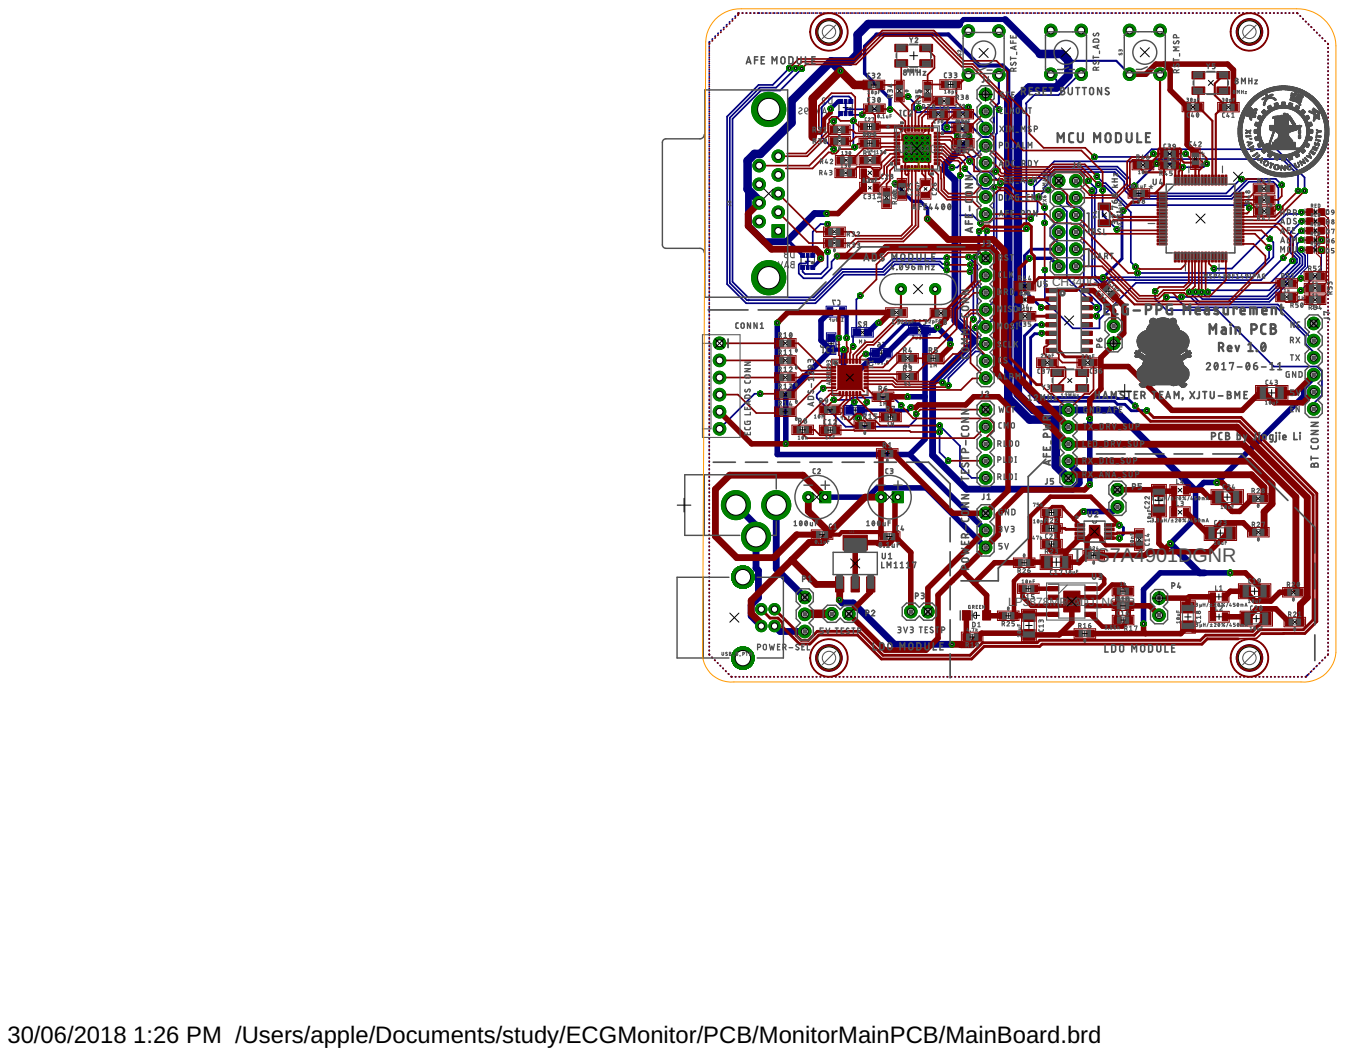
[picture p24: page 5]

30/06/2018 1:26 PM /Users/apple/Documents/study/ECGMonitor/PCB/MonitorMainPCB/MainBoard.brd

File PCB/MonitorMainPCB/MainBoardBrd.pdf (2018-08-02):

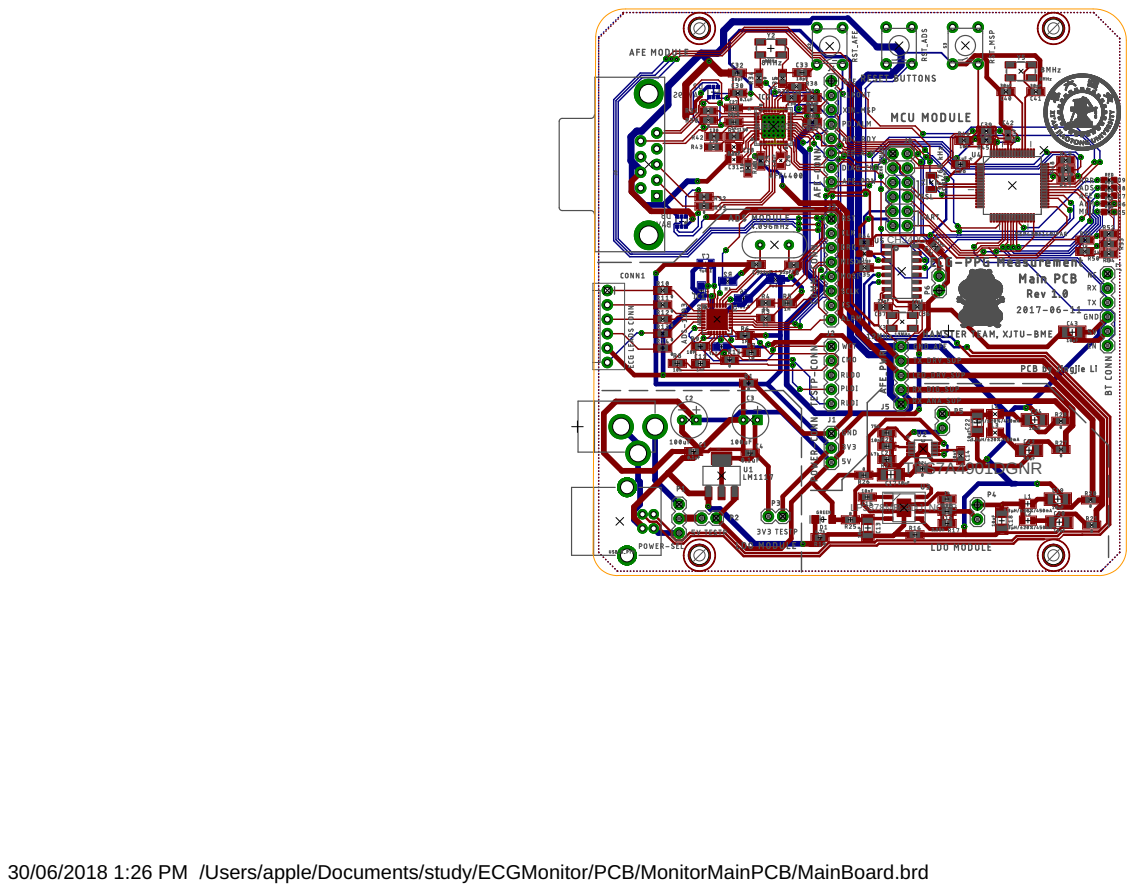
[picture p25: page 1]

30/06/2018 1:26 PM /Users/apple/Documents/study/ECGMonitor/PCB/MonitorMainPCB/MainBoard.brd

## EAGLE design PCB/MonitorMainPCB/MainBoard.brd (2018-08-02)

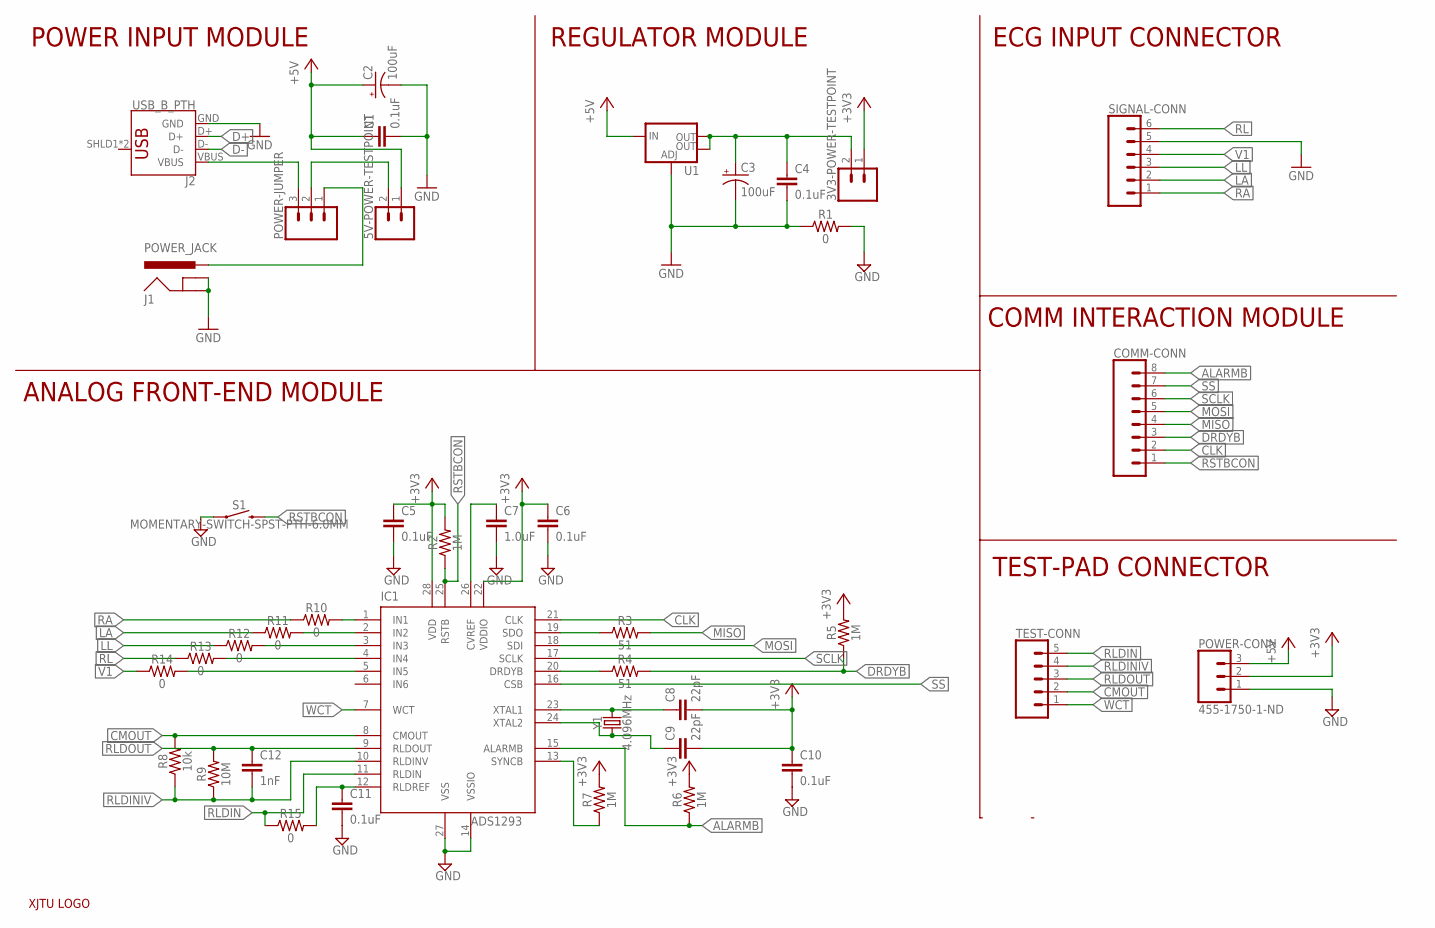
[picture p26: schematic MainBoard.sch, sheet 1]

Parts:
3V3-POWER-TESTPOINT, 5V-POWER-TESTPOINT: CONN_02; 1X02
C1, C4, C5, C6, C10, C11: 0.1uF; 0603
C2, C3: 100uF; CPOL-RADIAL-2.5MM-6.5MM
C7: 1.0uF; 0805
C8, C9: 22pF; 0603
C12: 1nF; 0603
COMM-CONN: CONN_08"; 1X08
IC1: ADS1293; QFN28-5X5
J1: POWER_JACK; POWER_JACK_PTH
J2: USB_B_PTH; USB-B-PTH
POWER-CONN: 455-1750-1-ND; 1X03
POWER-JUMPER: CONN_03; 1X03
R1, R10, R11, R12, R13, R14, R15: 0; 0603
R2, R5, R6, R7: 1M; 0603
R3, R4: 51; 0603
R8: 10k; 0603
R9: 10M; 0603
S1: MOMENTARY-SWITCH-SPST-PTH-6.0MM; TACTILE_SWITCH_PTH_6.0MM
SIGNAL-CONN: CONN_06POLAR; MOLEX-1X6
TEST-CONN: CONN_05; 1X05
U1: V_REG_LM1117SOT223; SOT223
U$6: XJTULOGO
Y1: 4.096MHz; HC49US

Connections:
+3V3: 3V3-POWER-TESTPOINT.1, C5.1, C6.1, C8.2, C9.2, C10.1, IC1.22 (VDDIO), IC1.28 (VDD), POWER-CONN.2, R2.2, R5.2, R6.2, R7.2; also elsewhere on the board
+5V: 5V-POWER-TESTPOINT.1, C1.1, C2.1 (+), POWER-CONN.3, U1.3 (IN); also elsewhere on the board
ALARMB: COMM-CONN.8, IC1.15 (ALARMB), R6.1; also elsewhere on the board
CLK: COMM-CONN.2, IC1.21 (CLK)
CMOUT: IC1.8 (CMOUT), R8.2, TEST-CONN.2
D+: J2.D+; also elsewhere on the board
D-: J2.D-; also elsewhere on the board
DRDYB: COMM-CONN.3, R4.2, R5.1; also elsewhere on the board
GND: C1.2, C2.2 (-), C3.2 (-), C4.2, C5.2, C6.2, C7.2, C10.2, C11.2, IC1.14 (VSSIO), IC1.27 (VSS), J1.GND, J1.GNDBREAK, J2.GND, POWER-CONN.1, R1.1, R1.2, S1.1, SIGNAL-CONN.5, U1.1 (ADJ); also elsewhere on the board
LA: R11.1, SIGNAL-CONN.2
LL: R12.1, SIGNAL-CONN.3
MISO: COMM-CONN.4, R3.2; also elsewhere on the board
MOSI: COMM-CONN.5, IC1.18 (SDI); also elsewhere on the board
unnamed: C7.1, IC1.26 (CVREF)
unnamed: J2.VBUS, POWER-JUMPER.3
unnamed: J1.PWR, POWER-JUMPER.1
unnamed: C8.1, IC1.23 (XTAL1), Y1.2
unnamed: C9.1, IC1.24 (XTAL2), Y1.1
unnamed: IC1.19 (SDO), R3.1
unnamed: IC1.20 (DRDYB), R4.1
unnamed: IC1.13 (SYNCB), R7.1
unnamed: C11.1, IC1.12 (RLDREF), R15.2
unnamed: IC1.1 (IN1), R10.2
unnamed: IC1.2 (IN2), R11.2
unnamed: IC1.3 (IN3), R12.2
unnamed: IC1.4 (IN4), R13.2
unnamed: IC1.5 (IN5), R14.2
unnamed: 5V-POWER-TESTPOINT.2, POWER-JUMPER.2
unnamed: 3V3-POWER-TESTPOINT.2, C3.1 (+), C4.1, U1.2 (OUT), U1.4 (OUT)
RA: R10.1, SIGNAL-CONN.1
RL: R13.1, SIGNAL-CONN.6
RLDIN: IC1.11 (RLDIN), R15.1, TEST-CONN.5
RLDINIV: C12.2, IC1.10 (RLDINV), R8.1, R9.1, TEST-CONN.4
RLDOUT: C12.1, IC1.9 (RLDOUT), R9.2, TEST-CONN.3
RSTBCON: COMM-CONN.1, IC1.25 (RSTB), R2.1, S1.3 (2)
SCLK: COMM-CONN.6, IC1.17 (SCLK); also elsewhere on the board
SS: COMM-CONN.7, IC1.16 (CSB); also elsewhere on the board
V1: R14.1, SIGNAL-CONN.4
WCT: IC1.7 (WCT), TEST-CONN.1

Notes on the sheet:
POWER INPUT MODULE
REGULATOR MODULE
ECG INPUT CONNECTOR
ANALOG FRONT-END MODULE
COMM INTERACTION MODULE
TEST-PAD CONNECTOR

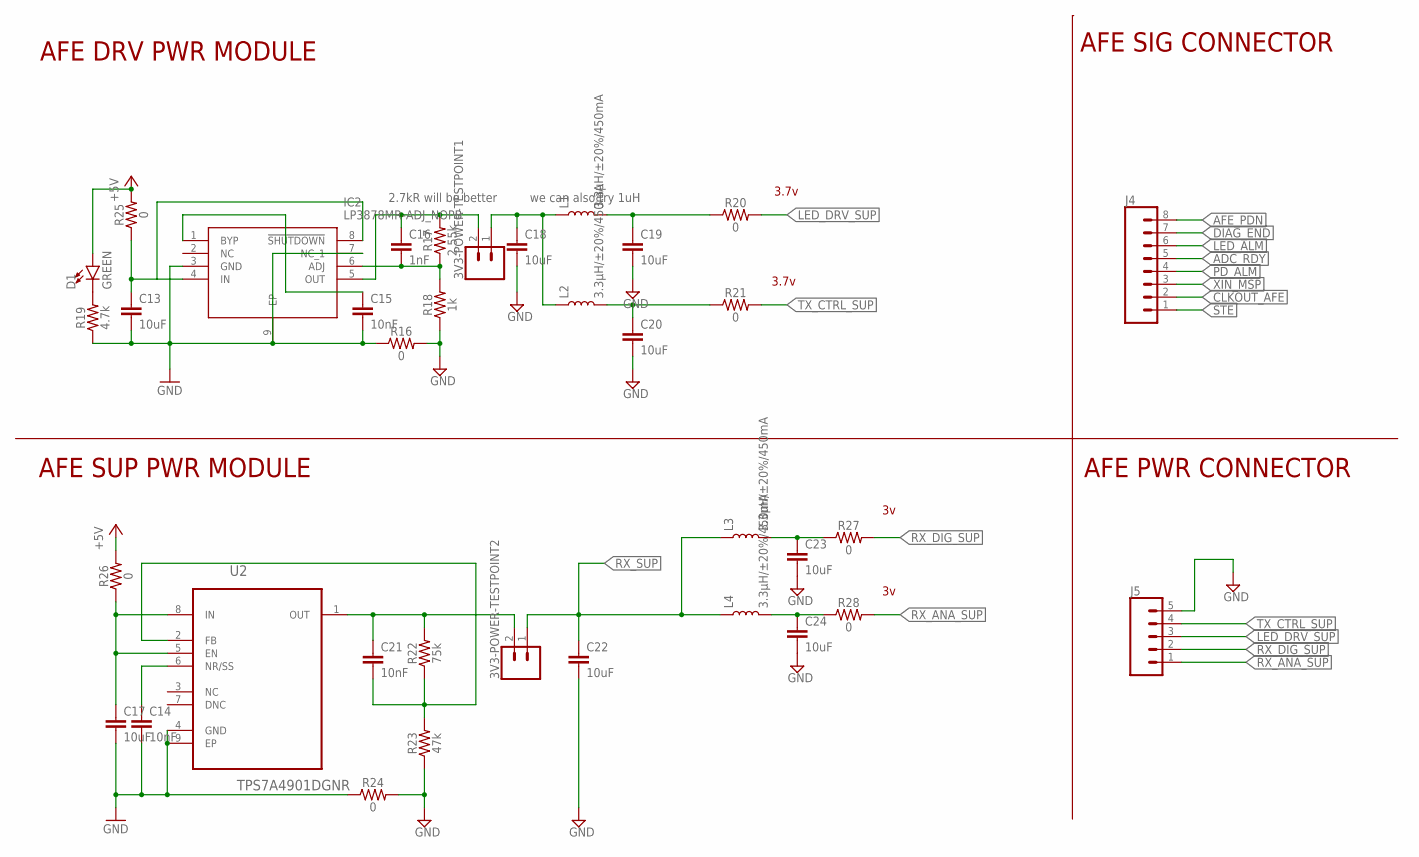
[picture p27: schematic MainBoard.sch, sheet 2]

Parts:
3V3-POWER-TESTPOINT1, 3V3-POWER-TESTPOINT2: CONN_02; 1X02
C13, C17, C18, C19, C20, C22, C23, C24: 10uF; 1206
C14, C15, C21: 10nF; 0603
C16: 1nF; 0603
D1: GREEN; LED-1206
IC2: LP3878MR-ADJ_NOPB; SOIC127P602X168-9N
J4: CONN_08"; 1X08
J5: CONN_05; 1X05
L1, L2, L3, L4: 3.3µH/±20%/450mA; 0805
R16, R20, R21, R24, R25, R26, R27, R28: 0; 0603
R17: 2.55k; 0603
R18: 1k; 0603
R19: 4.7k; 0603
R22: 75k; 0603
R23: 47k; 0603
U2: TPS7A4901DGNR; SOP65P490X110-9N

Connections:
+5V: D1.A, R25.2, R26.2; also elsewhere on the board
ADC_RDY: J4.5; also elsewhere on the board
AFE_PDN: J4.8; also elsewhere on the board
CLKOUT_AFE: J4.2; also elsewhere on the board
DIAG_END: J4.7; also elsewhere on the board
GND: C13.2, C14.2, C15.2, C17.2, C18.2, C19.2, C20.2, C22.2, C23.2, C24.2, IC2.3 (GND), IC2.7 (NC_1), IC2.9 (EP), J5.5, R16.1, R16.2, R18.1, R19.1, R23.1, R24.1, R24.2, U2.4 (GND), U2.9 (EP); also elsewhere on the board
LED_ALM: J4.6; also elsewhere on the board
LED_DRV_SUP: J5.3, R20.2; also elsewhere on the board
unnamed: D1.C, R19.2
unnamed: 3V3-POWER-TESTPOINT1.1, C18.1, L1.1, L2.1
unnamed: C16.2, IC2.6 (ADJ), R17.1, R18.2
unnamed: C15.1, IC2.1 (BYP)
unnamed: 3V3-POWER-TESTPOINT1.2, C16.1, IC2.5 (OUT), R17.2
unnamed: C14.1, U2.6 (NR/SS)
unnamed: C19.1, L1.2, R20.1
unnamed: C20.1, L2.2, R21.1
unnamed: C17.1, R26.1, U2.5 (EN), U2.8 (IN)
unnamed: 3V3-POWER-TESTPOINT2.2, C21.1, R22.2, U2.1 (OUT)
unnamed: C21.2, R22.1, R23.2, U2.2 (FB)
unnamed: C23.1, L3.2, R27.1
unnamed: C13.1, IC2.4 (IN), IC2.8 (!SHUTDOWN), R25.1
unnamed: C24.1, L4.2, R28.1
PD_ALM: J4.4; also elsewhere on the board
RX_ANA_SUP: J5.1, R28.2; also elsewhere on the board
RX_DIG_SUP: J5.2, R27.2; also elsewhere on the board
RX_SUP: 3V3-POWER-TESTPOINT2.1, C22.1, L3.1, L4.1
STE: J4.1; also elsewhere on the board
TX_CTRL_SUP: J5.4, R21.2; also elsewhere on the board
XIN_MSP: J4.3; also elsewhere on the board

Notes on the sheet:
2.7kR will be better
we can also try 1uH
AFE SUP PWR MODULE
AFE DRV PWR MODULE
AFE SIG CONNECTOR
AFE PWR CONNECTOR
3.7v

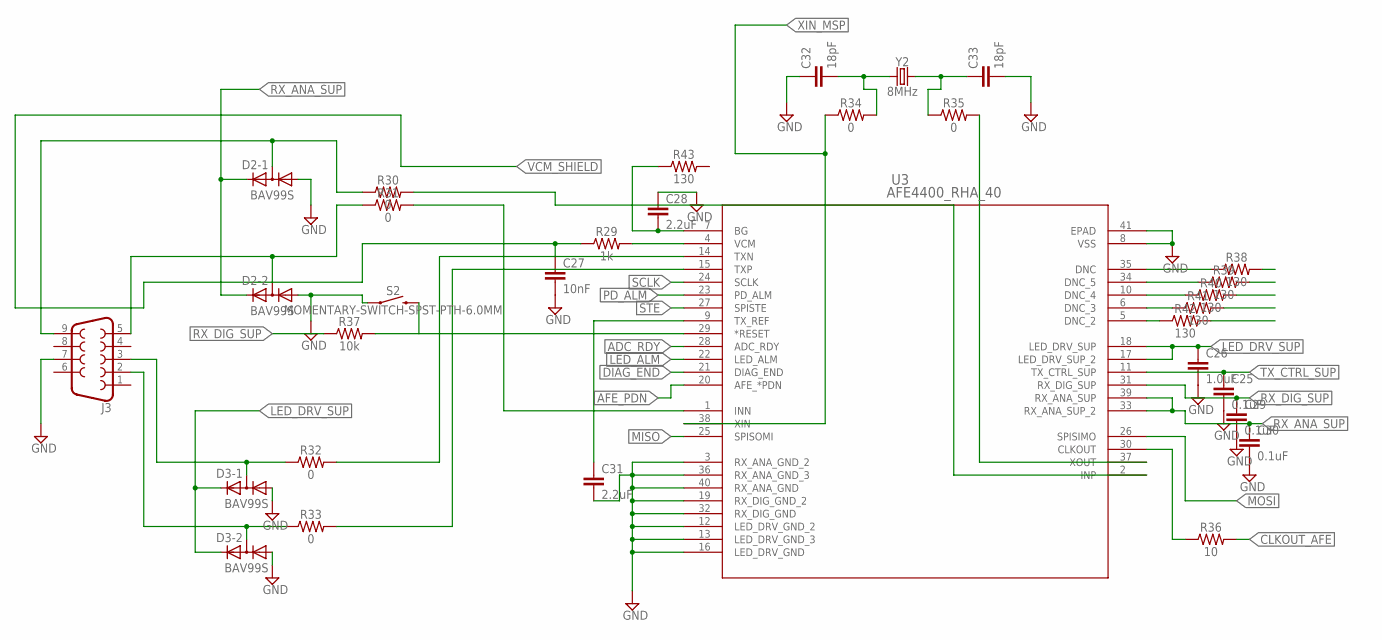
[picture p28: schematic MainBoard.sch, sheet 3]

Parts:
C25, C29, C30: 0.1uF; 0603
C26: 1.0uF; 0805
C27: 10nF; 0603
C28, C31: 2.2uF; 0805
C32, C33: 18pF; 0603
D2, D3: BAV99S; SOT363
J3: DB9FEMALE; DB9
R29: 1k; 0603
R30, R31, R32, R33, R34, R35: 0; 0603
R36: 10; 0603
R37: 10k; 0603
R38, R39, R40, R41, R42, R43: 130; 0603
S2: MOMENTARY-SWITCH-SPST-PTH-6.0MM; TACTILE_SWITCH_PTH_6.0MM
U3: AFE4400_RHA_40; RHA40_4P15X4P15
Y2: 8MHz; CRYSTAL-SMD-5X3.2-4PAD

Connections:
ADC_RDY: U3.28 (ADC_RDY); also elsewhere on the board
AFE_PDN: U3.20 (AFE_*PDN); also elsewhere on the board
CLKOUT_AFE: R36.2; also elsewhere on the board
DIAG_END: U3.21 (DIAG_END); also elsewhere on the board
GND: C25.2, C26.2, C27.2, C28.1, C29.2, C30.2, C31.2, C32.1, C33.2, D2.1 (A1), D2.4 (A1), D3.1 (A1), D3.4 (A1), J3.7, S2.1, U3.3 (RX_ANA_GND_2), U3.8 (VSS), U3.12 (LED_DRV_GND_2), U3.13 (LED_DRV_GND_3), U3.16 (LED_DRV_GND), U3.19 (RX_DIG_GND_2), U3.32 (RX_DIG_GND), U3.36 (RX_ANA_GND_3), U3.40 (RX_ANA_GND), U3.41 (EPAD); also elsewhere on the board
LED_ALM: U3.22 (LED_ALM); also elsewhere on the board
LED_DRV_SUP: C26.1, D3.2 (K2), D3.5 (K2), U3.17 (LED_DRV_SUP_2), U3.18 (LED_DRV_SUP); also elsewhere on the board
MISO: U3.25 (SPISOMI); also elsewhere on the board
MOSI: U3.26 (SPISIMO); also elsewhere on the board
unnamed: C28.2, R43.1, U3.7 (BG)
unnamed: C31.1, U3.9 (TX_REF)
unnamed: R32.2, U3.14 (TXN)
unnamed: R29.2, U3.4 (VCM)
unnamed: R31.2, U3.1 (INN)
unnamed: R30.2, U3.2 (INP)
unnamed: D2.3 (K1A2), J3.5, R31.1
unnamed: D2.6 (K1A2), J3.9, R30.1
unnamed: R33.2, U3.15 (TXP)
unnamed: D3.6 (K1A2), J3.3, R32.1
unnamed: D3.3 (K1A2), J3.2, R33.1
unnamed: C32.2, R34.2, Y2.1
unnamed: C33.1, R35.1, Y2.3 (2)
unnamed: R36.1, U3.30 (CLKOUT)
unnamed: R37.2, S2.3 (2), U3.29 (*RESET)
unnamed: R35.2, U3.37 (XOUT)
unnamed: R38.1, U3.35 (DNC)
unnamed: R42.1, U3.5 (DNC_2)
unnamed: R41.1, U3.6 (DNC_3)
unnamed: R40.1, U3.10 (DNC_4)
unnamed: R39.1, U3.34 (DNC_5)
PD_ALM: U3.23 (PD_ALM); also elsewhere on the board
RX_ANA_SUP: C30.1, D2.2 (K2), D2.5 (K2), U3.33 (RX_ANA_SUP_2), U3.39 (RX_ANA_SUP); also elsewhere on the board
RX_DIG_SUP: C29.1, R37.1, U3.31 (RX_DIG_SUP); also elsewhere on the board
SCLK: U3.24 (SCLK); also elsewhere on the board
STE: U3.27 (SPISTE); also elsewhere on the board
TX_CTRL_SUP: C25.1, U3.11 (TX_CTRL_SUP); also elsewhere on the board
VCM_SHIELD: C27.1, R29.1
XIN_MSP: R34.1, U3.38 (XIN); also elsewhere on the board

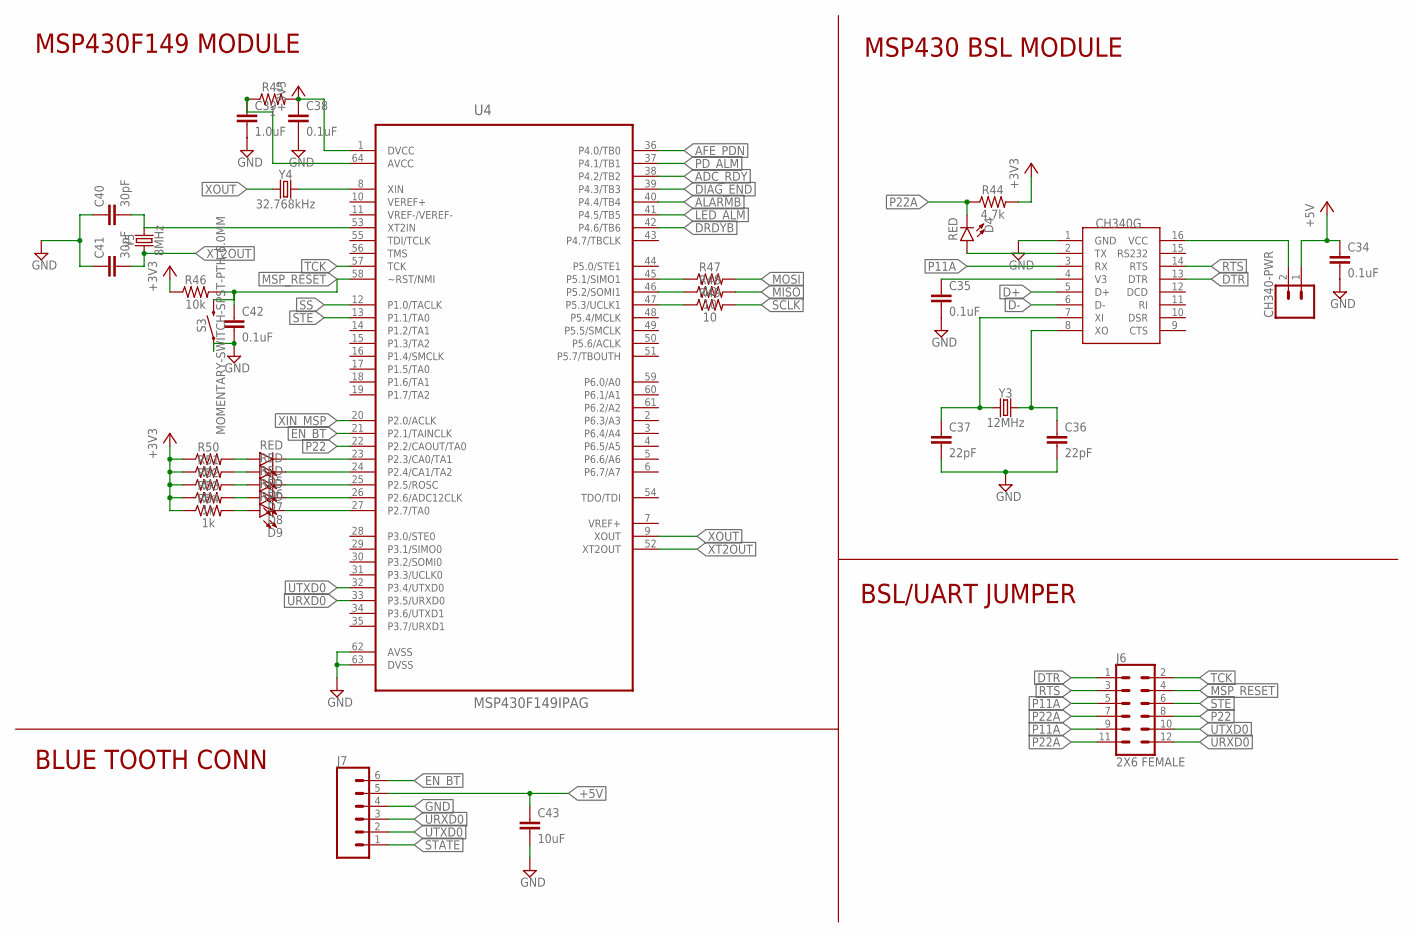
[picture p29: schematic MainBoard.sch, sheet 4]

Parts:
C34, C35, C38, C42: 0.1uF; 0603
C36, C37: 22pF; 0603
C39: 1.0uF; 0603
C40, C41: 30pF; 0603
C43: 10uF; 1206
CH340-PWR: CONN_02; 1X02
D4, D5, D6, D7, D8, D9: RED; LED-0603
J6: 2X6 FEMALE; 2X6
J7: CONN_06SILK_FEMALE_PTH; 1X06
R44: 4.7k; 0603
R45: 1; 0603
R46: 10k; 0603
R47, R48, R49: 10; 0603
R50, R51, R52, R53, R54: 1k; 0603
S3: MOMENTARY-SWITCH-SPST-PTH-6.0MM; TACTILE_SWITCH_PTH_6.0MM
U4: MSP430F149IPAG; QFP50P1200X1200X120-64N
U$5: CH340G; SOIC16
Y3: 12MHz; CRYSTAL-SMD-5X3.2-4PAD
Y4: 32.768kHz; CRYSTAL-SMD-3.2X1.5MM
Y5: 8MHz; CRYSTAL-SMD-5X3.2-4PAD

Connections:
+3V3: C38.1, R44.2, R45.2, R46.1, R50.1, R51.1, R52.1, R53.1, R54.1, U4.1 (DVCC); also elsewhere on the board
+5V: C34.1, C43.1, CH340-PWR.1, J7.5; also elsewhere on the board
ADC_RDY: U4.38 (P4.2/TB2); also elsewhere on the board
AFE_PDN: U4.36 (P4.0/TB0); also elsewhere on the board
ALARMB: U4.40 (P4.4/TB4); also elsewhere on the board
D+: U$5.5 (D+); also elsewhere on the board
D-: U$5.6 (D-); also elsewhere on the board
DIAG_END: U4.39 (P4.3/TB3); also elsewhere on the board
DRDYB: U4.42 (P4.6/TB6); also elsewhere on the board
DTR: J6.1, U$5.13 (DTR)
EN_BT: J7.6, U4.21 (P2.1/TAINCLK)
GND: C34.2, C35.2, C36.2, C37.2, C38.2, C39.2, C40.1, C41.1, C42.2, C43.2, J7.4, S3.1, U4.62 (AVSS), U4.63 (DVSS), U$5.1 (GND); also elsewhere on the board
LED_ALM: U4.41 (P4.5/TB5); also elsewhere on the board
MISO: R48.2; also elsewhere on the board
MOSI: R47.2; also elsewhere on the board
MSP_RESET: C42.1, J6.4, R46.2, S3.3 (2), U4.58 (~RST/NMI)
unnamed: C39.1, R45.1, U4.64 (AVCC)
unnamed: R47.1, U4.45 (P5.1/SIMO1)
unnamed: C35.1, U$5.4 (V3)
unnamed: D4.A, U$5.2 (TX)
unnamed: U4.8 (XIN), Y4.P$2 (2)
unnamed: C40.2, U4.53 (XT2IN), Y5.3 (2)
unnamed: R48.1, U4.46 (P5.2/SOMI1)
unnamed: R49.1, U4.47 (P5.3/UCLK1)
unnamed: D5.C, U4.23 (P2.3/CA0/TA1)
unnamed: D6.C, U4.24 (P2.4/CA1/TA2)
unnamed: D7.C, U4.25 (P2.5/ROSC)
unnamed: D8.C, U4.26 (P2.6/ADC12CLK)
unnamed: D9.C, U4.27 (P2.7/TA0)
unnamed: D5.A, R50.2
unnamed: D6.A, R51.2
unnamed: D7.A, R52.2
unnamed: D8.A, R53.2
unnamed: D9.A, R54.2
unnamed: CH340-PWR.2, U$5.16 (VCC)
P11A: J6.5, J6.9, U$5.3 (RX)
P22: J6.8, U4.22 (P2.2/CAOUT/TA0)
P22A: D4.C, J6.7, J6.11, R44.1
PD_ALM: U4.37 (P4.1/TB1); also elsewhere on the board
RTS: J6.3, U$5.14 (RTS)
SCLK: R49.2; also elsewhere on the board
SS: U4.12 (P1.0/TACLK); also elsewhere on the board
STATE: J7.1
STE: J6.6, U4.13 (P1.1/TA0); also elsewhere on the board
TCK: J6.2, U4.57 (TCK)
URXD0: J6.12, J7.3, U4.33 (P3.5/URXD0)
UTXD0: J6.10, J7.2, U4.32 (P3.4/UTXD0)
XI: C37.1, U$5.7 (XI), Y3.1
XIN_MSP: U4.20 (P2.0/ACLK); also elsewhere on the board
XO: C36.1, U$5.8 (XO), Y3.3 (2)
XOUT: U4.9 (XOUT), Y4.P$1 (1)
XT2OUT: C41.2, U4.52 (XT2OUT), Y5.1

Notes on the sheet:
MSP430F149 MODULE
MSP430 BSL MODULE
BSL/UART JUMPER
BLUE TOOTH CONN

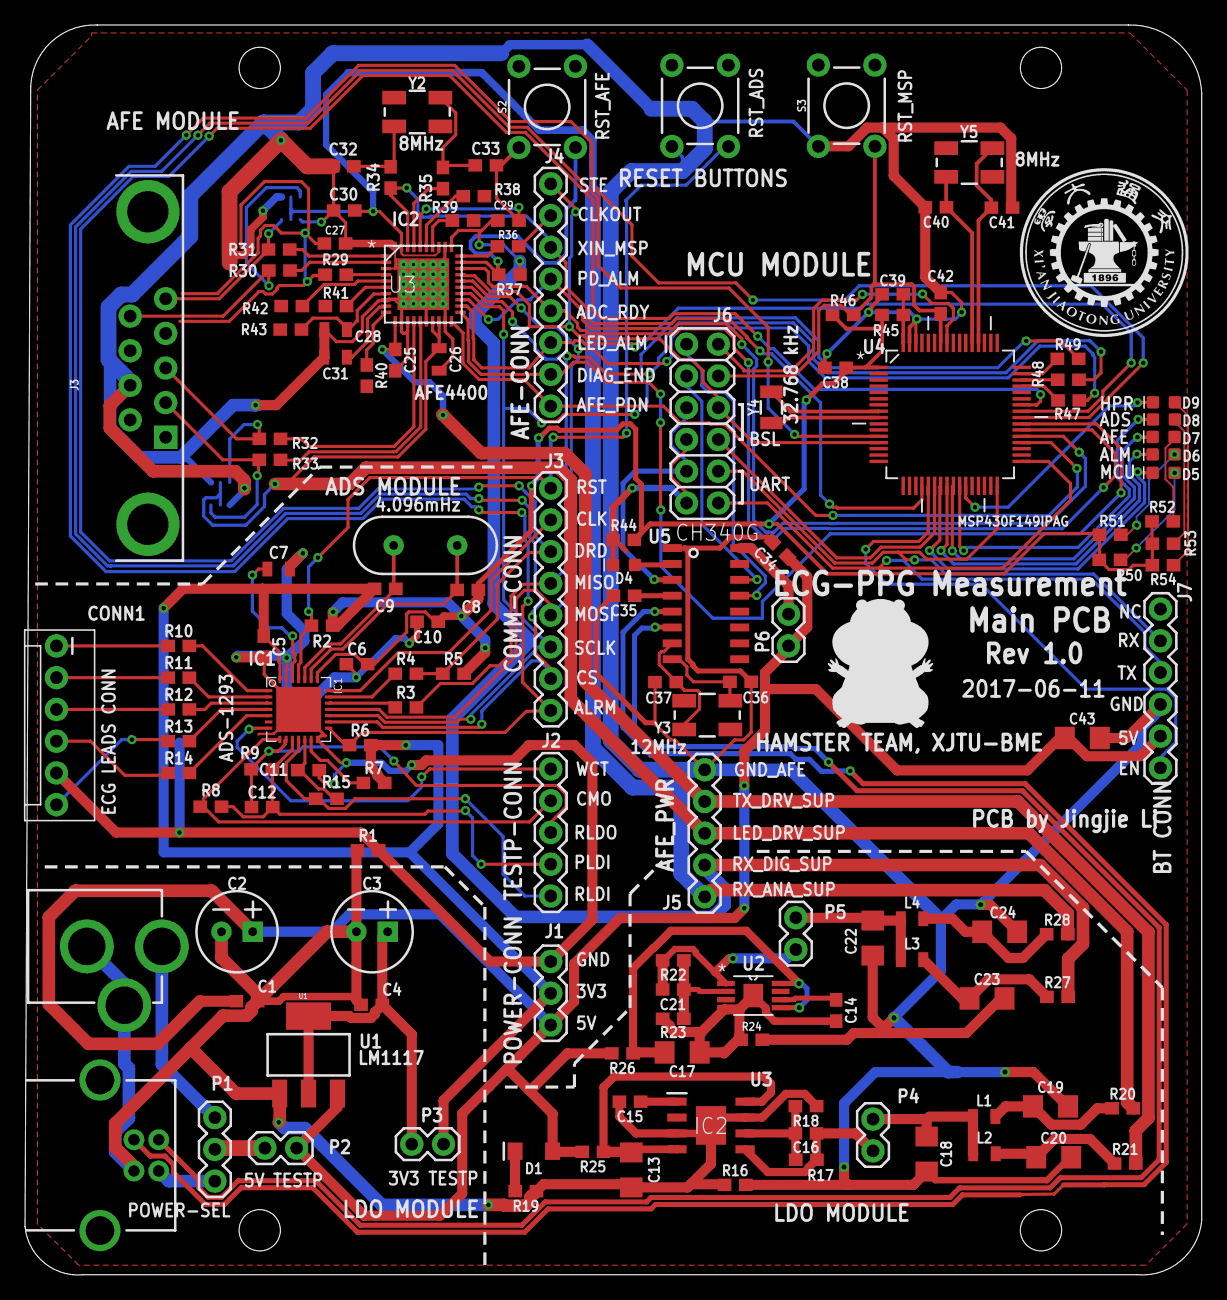
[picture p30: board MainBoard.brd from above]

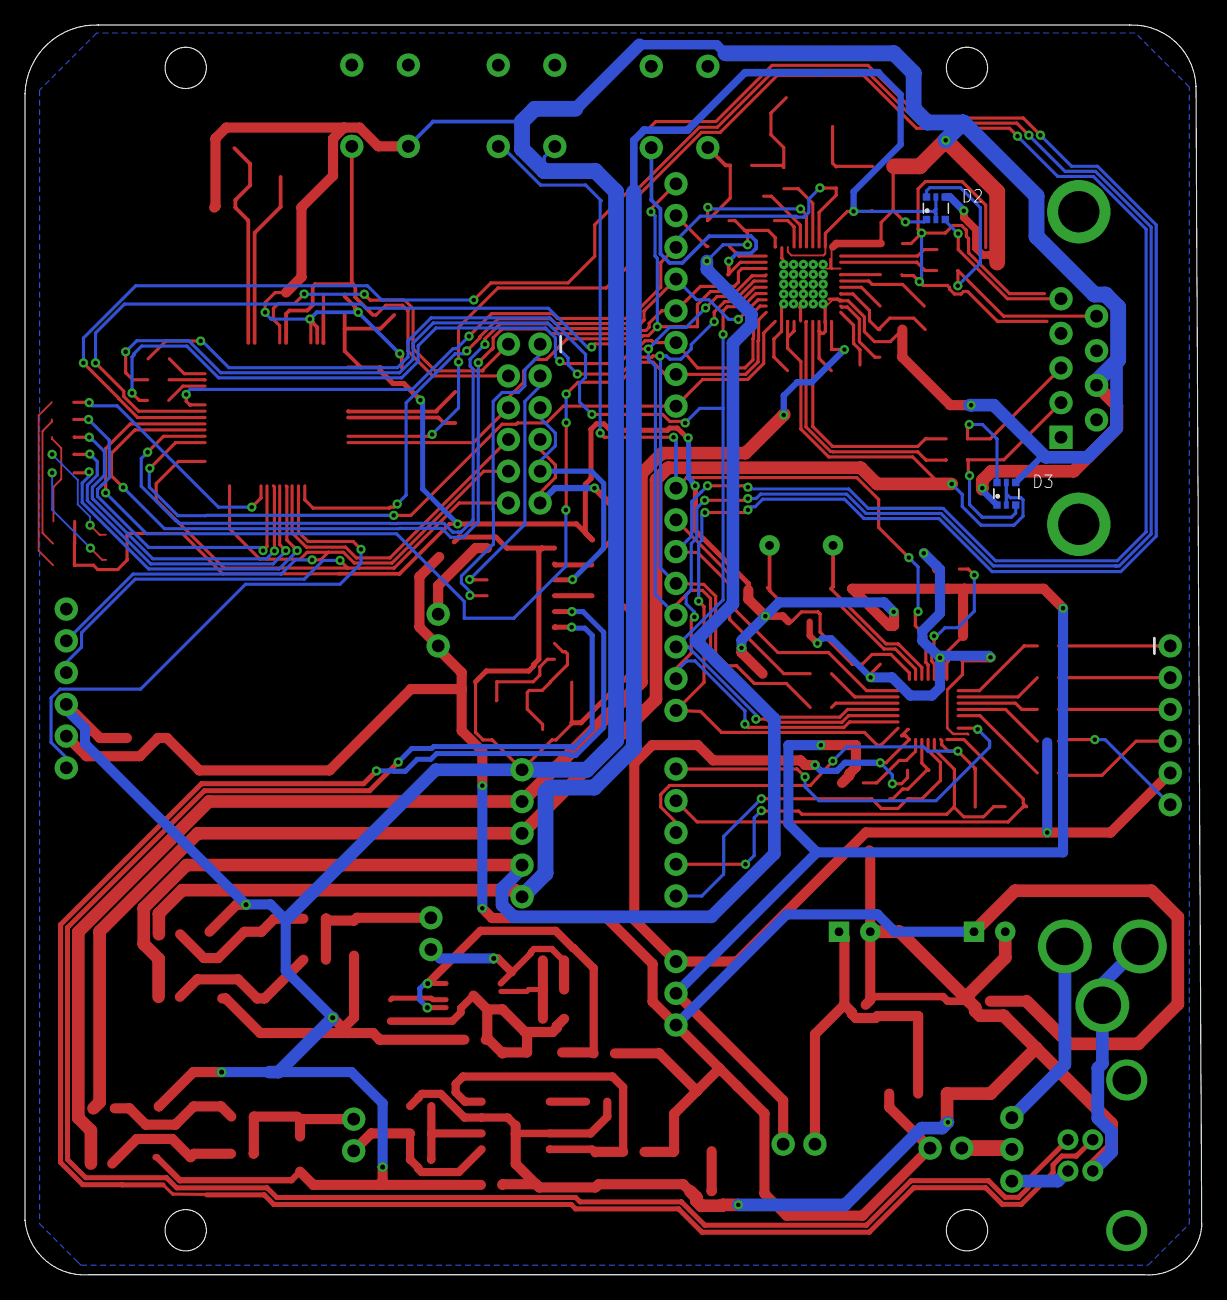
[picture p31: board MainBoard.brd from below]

Board: 2 copper layers, 94.1 x 100.0 mm, 148 parts (2 on the bottom side), 121 nets.

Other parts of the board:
U$1, U$2, U$3, U$4: STAND-OFF
U$7: HAMSTERLOGO

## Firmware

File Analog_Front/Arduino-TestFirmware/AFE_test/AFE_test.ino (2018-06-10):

#include <SPI.h>
byte LowByte = 0;
byte SecondByte = 0;
//unsigned char SPIval16[5]={0xD0,0x01,0x12,0x35,0x0A};
unsigned long SPIval16[2]={22,22};
int SUPhighInt=0;
int highInt=0;
int midInt=0;
int lowInt=0;
unsigned int readstuff=0;
unsigned long receivedVal=0;

unsigned int receivedSupUpper=0;
unsigned int receivedUpper=0;
unsigned int receivedMiddle=0;
unsigned int receivedLower=0;

unsigned int CH1EcgData=0;
unsigned int CH2EcgData=0;
unsigned int CH3EcgData=0;

byte OutputType = 0;
byte OutputTypeS = 0;

byte AFEwriteVal[3]={0x00,0x00,0x00};

const byte READ = 0b10000000;   //  read command
const byte WRITE = 0b00000000;   //  write command

void setup() {
  // put your setup code here, to run once:
  SerialUSB.begin(115200);
  SerialUSB.println("Starting SPI\n");
  SPI.begin(4);
  SPI.setClockDivider(4, 21); 
  SPI.setBitOrder(MSBFIRST);
  SPI.setDataMode(SPI_MODE2);
  
}

void loop() {
  // put your main code here, to run repeatedly:

  if(OutputType=='Q'||OutputType==0){
    SerialUSB.println("We do what? (A-AFEWite,B-AFERead,E-InitilizeAFE,F-ReadAFEData,W-WriteSPI,R-ReadSPI,D-StartGetData,N-NormalConfig,S-StartConversition,T-StopConversition,Z-null)\n");
    while (SerialUSB.available() == 0) {}
    OutputType = SerialUSB.read();
  }
  switch(OutputType) {
    case 'W': {
      SerialUSB.println("#Write State!,you can trpe Q to quit");
      SerialUSB.print("Input Addr:  ");
      while (SerialUSB.available() == 0) {}
      OutputTypeS=SerialUSB.read();
      if(OutputTypeS=='Q'){
        OutputType=OutputTypeS;
        while(Serial.read() >=0){}
      }
      else{
        lowInt=OutputTypeS-'0';
        SerialUSB.print(lowInt);
        while (SerialUSB.available() == 0) {}
        midInt=SerialUSB.read()-'0';
        SerialUSB.print(midInt);
        while (SerialUSB.available() == 0) {}
        highInt=SerialUSB.read()-'0';
        SerialUSB.print(highInt);
        SerialUSB.print("\n");
        // get some numbers
        SPIval16[0]=100*lowInt+10*midInt+highInt;
  
        SerialUSB.print("Input Data:  ");
  
  
        while (SerialUSB.available() == 0) {}
        lowInt=SerialUSB.read()-'0';
        SerialUSB.print(lowInt);
        while (SerialUSB.available() == 0) {}
        midInt=SerialUSB.read()-'0';
        SerialUSB.print(midInt);
        while (SerialUSB.available() == 0) {}
        highInt=SerialUSB.read()-'0';
        SerialUSB.print(highInt);
        SerialUSB.print("\n");
        // get some numbers
        SPIval16[1]=100*lowInt+10*midInt+highInt;
        
        SerialUSB.print("Now We are going to write:");
        SerialUSB.print(SPIval16[0],HEX);
        SerialUSB.print(" ");
        SerialUSB.print(SPIval16[1],HEX);
        SerialUSB.print("\n");
        //SPI.transfer(4,SPIval16[0],SPI_CONTINUE);
        //SPI.transfer(4,SPIval16[1]);
        writeRegister(4,SPIval16[0],SPIval16[1]);
        
      }
      break;
    }
    case 'N': {
      writeRegister(4,0x01,0x11);
      writeRegister(4,0x02,0x19);
      writeRegister(4,0x03,0x2E);
      writeRegister(4,0x0A,0x07);
      writeRegister(4,0x0C,0x04);

      writeRegister(4,0x0D,0x01);
      writeRegister(4,0x0E,0x02);
      writeRegister(4,0x0F,0x03);
      
      writeRegister(4,0x10,0x01);

      writeRegister(4,0x12,0x04);
      writeRegister(4,0x21,0x02);
      writeRegister(4,0x22,0x02);
      writeRegister(4,0x23,0x02);
      writeRegister(4,0x24,0x02);
      writeRegister(4,0x27,0x08);
      writeRegister(4,0x2F,0x70);

      SerialUSB.println("#ADS Initilized!");
      OutputType = 0;
      break;
    }
    
    case 'S': {//start conversion
      SerialUSB.println("#Start Conversion!");
      writeRegister(4,0x00,0x01);
      //SPI.transfer(4,0x00,SPI_CONTINUE);
      //SPI.transfer(4,0x01);
      OutputType='Q';
      break;
    }
    
    case 'T': {//stop conversion
      SerialUSB.println("#Stop Conversion!");
      writeRegister(4,0x00,0x00);
      //SPI.transfer(4,0x00,SPI_CONTINUE);
      //SPI.transfer(4,0x00);
      OutputType='Q';
      break;
    }
    
    case 'R':{ //
      SerialUSB.println("#Read from Addr State! You can type in Q to quit this state");
      SerialUSB.print("Addr: ");
      while (SerialUSB.available() == 0) {}
      OutputTypeS=SerialUSB.read();
      if(OutputTypeS=='Q'){
        OutputType=OutputTypeS;
        while(Serial.read() >=0){}
      }
      else{
        lowInt=OutputTypeS-'0';
        //SerialUSB.print(lowInt);
        while (SerialUSB.available() == 0) {}
        midInt=SerialUSB.read()-'0';
        //SerialUSB.print(midInt);
        while (SerialUSB.available() == 0) {}
        highInt=SerialUSB.read()-'0';
        //SerialUSB.print(highInt);
        // get some numbers
        SPIval16[0]=100*lowInt+10*midInt+highInt;
        SerialUSB.print("0x");
        SerialUSB.print(SPIval16[0],HEX);
        SerialUSB.print("   ");
        //SPI.transfer(4,SPIval16[0],SPI_CONTINUE);
        //receivedVal = SPI.transfer(4,0x00);
        
        receivedVal=readRegister(4,SPIval16[0]);
        
        SerialUSB.print("we got:");
        SerialUSB.print(receivedVal,HEX);
        SerialUSB.print("\n");
      }
      break;
    }
    
    case 'Z':{
      SerialUSB.println("null state");
      OutputType='Q';
      break;
      
    }

    case 'D':{
      SerialUSB.println("Now we are going to start steaming reading");

      while (SerialUSB.available() == 0) {
        //SPI.transfer(4,SPIval16[0],SPI_CONTINUE);
        SPI.transfer(4,0xD0,SPI_CONTINUE);
        
        receivedUpper = SPI.transfer(4,0x00,SPI_CONTINUE);//0x37
        receivedMiddle = SPI.transfer(4,0x00,SPI_CONTINUE);//0x38
        receivedLower = SPI.transfer(4,0x00,SPI_CONTINUE);//0x39
  
        CH1EcgData=256*256*receivedUpper+256*receivedMiddle+receivedLower;
        
        receivedUpper = SPI.transfer(4,0x00,SPI_CONTINUE);//0x3A
        receivedMiddle = SPI.transfer(4,0x00,SPI_CONTINUE);//0x3B
        receivedLower = SPI.transfer(4,0x00,SPI_CONTINUE);//0x3C
  
        CH2EcgData=256*256*receivedUpper+256*receivedMiddle+receivedLower;
  
        receivedUpper = SPI.transfer(4,0x00,SPI_CONTINUE);//0x3D
        receivedMiddle = SPI.transfer(4,0x00,SPI_CONTINUE);//0x3E
        receivedLower = SPI.transfer(4,0x00);//0x3F
  
        CH3EcgData=256*256*receivedUpper+256*receivedMiddle+receivedLower;
  
        SerialUSB.print("ECG Channel I Data: ");
        SerialUSB.print(CH1EcgData-2000);
        SerialUSB.print(" ECG Channel II Data: ");
        SerialUSB.print(CH2EcgData);
        SerialUSB.print(" ECG Channel III Data: ");
        //SerialUSB.print(CH3EcgData+2000);
        SerialUSB.print(" \n");

        delay(5);
      
      }
      OutputType = SerialUSB.read();
      break;
    }
    case 'A':{ //AFE Write
      DisableAFERead(4);
      SerialUSB.println("#AFE Write!,you can trpe Q to quit");
      SerialUSB.print("Input Addr:  ");
      while (SerialUSB.available() == 0) {}
      OutputTypeS=SerialUSB.read();
      if(OutputTypeS=='Q'){
        OutputType=OutputTypeS;
        while(Serial.read() >=0){}
      }
      else{
        lowInt=OutputTypeS-'0';
        SerialUSB.print(lowInt);
        while (SerialUSB.available() == 0) {}
        midInt=SerialUSB.read()-'0';
        SerialUSB.print(midInt);
        while (SerialUSB.available() == 0) {}
        highInt=SerialUSB.read()-'0';
        SerialUSB.print(highInt);
        while (SerialUSB.available() == 0) {}
        SUPhighInt=SerialUSB.read()-'0';
        SerialUSB.print(SUPhighInt);
        SerialUSB.print("\n");
        // get some numbers
        SPIval16[0]=1000*lowInt+100*midInt+10*highInt+SUPhighInt;
  
        SerialUSB.print("Input Data:  ");
  
  
        while (SerialUSB.available() == 0) {}
        lowInt=SerialUSB.read()-'0';
        SerialUSB.print(lowInt);
        while (SerialUSB.available() == 0) {}
        midInt=SerialUSB.read()-'0';
        SerialUSB.print(midInt);
        while (SerialUSB.available() == 0) {}
        highInt=SerialUSB.read()-'0';
        SerialUSB.print(highInt);
        while (SerialUSB.available() == 0) {}
        SUPhighInt=SerialUSB.read()-'0';
        SerialUSB.print(SUPhighInt);
        SerialUSB.print("\n");
        // get some numbers
        SPIval16[1]=1000*lowInt+100*midInt+10*highInt+SUPhighInt;
        
        SerialUSB.print("Now We are going to write:");
        SerialUSB.print(SPIval16[0],HEX);
        SerialUSB.print("  ");
        SerialUSB.print(lowInt);
        SerialUSB.print(midInt);
        SerialUSB.print(highInt);
        SerialUSB.print("\n");

        AFE4400_Set_Register(4,SPIval16[0],SPIval16[1]);
        //byte toWrite[3]={highInt,midInt,lowInt};
        //writeAFERegister(4,SPIval16[0],toWrite);
      }
      OutputType = 0;
      break;
    }
    case 'B':{ //AFE Read
      //EnableAFERead(4);
      AFE4400_Set_READABLE(4,1);
      SerialUSB.println("#Read from AFE Addr! You can type in Q to quit this state");
      SerialUSB.print("Addr: ");
      while (SerialUSB.available() == 0) {}
      OutputTypeS=SerialUSB.read();
      if(OutputTypeS=='Q'){
        OutputType=OutputTypeS;
        while(Serial.read() >=0){}
      }
      else{
        lowInt=OutputTypeS-'0';
        //SerialUSB.print(lowInt);
        while (SerialUSB.available() == 0) {}
        midInt=SerialUSB.read()-'0';
        //SerialUSB.print(midInt);
        while (SerialUSB.available() == 0) {}
        highInt=SerialUSB.read()-'0';
        while (SerialUSB.available() == 0) {}
        SUPhighInt=SerialUSB.read()-'0';
        //SerialUSB.print(highInt);
        // get some numbers
        SPIval16[0]=1000*lowInt+100*midInt+10*highInt+SUPhighInt;
        //SerialUSB.print("0x");
        SerialUSB.print(SPIval16[0]);
        SerialUSB.print("   ");

        receivedVal=AFE4400_Read_Register(4,SPIval16[0]);
        //receivedVal=readAFERegister(4,SPIval16[0]);
        
        SerialUSB.print("we got:");
        SerialUSB.print(receivedVal);
        SerialUSB.print("\n");
      }
      //DisableAFERead(4);
      AFE4400_Set_READABLE(4,0);
      OutputType = 0;
      break;
    }
    case 'E':{ //AFE Setup
      AFE4400_Set_READABLE(4,0);
      AFE4400_Set_Register(4,1,6050); //LED2STC
      AFE4400_Set_Register(4,2,7998); //LED2ENDC
      AFE4400_Set_Register(4,3,6000); //LED2LEDSTC
      AFE4400_Set_Register(4,4,7999); //LED2LEDENDC
      AFE4400_Set_Register(4,5,50);   //ALED2STC
      AFE4400_Set_Register(4,6,1998); //ALED2ENDC
      AFE4400_Set_Register(4,7,2050); //LED1STC
      AFE4400_Set_Register(4,8,3998); //LED1ENDC
      AFE4400_Set_Register(4,9,2000); //LED1LEDSTC
      AFE4400_Set_Register(4,10,3999); //LED1LEDENDC
      AFE4400_Set_Register(4,11,4050); //ALED1STC
      AFE4400_Set_Register(4,12,5998); //ALED1ENDC
      AFE4400_Set_Register(4,13,4); //LED2CONVST
      AFE4400_Set_Register(4,14,1999); //LED2CONVEND
      AFE4400_Set_Register(4,15,2004); //ALED2CONVST
      AFE4400_Set_Register(4,16,3999); //ALED2CONVEND
      AFE4400_Set_Register(4,17,4004); //LED1CONVST
      AFE4400_Set_Register(4,18,5999); //LED1CONVEND
      AFE4400_Set_Register(4,19,6004); //ALED1CONVST
      AFE4400_Set_Register(4,20,7999); // ALED1CONVEND

      AFE4400_Set_Register(4,21,0); //ADCRSTSTXT0
      AFE4400_Set_Register(4,22,3); //ADCRSTENDCT0
      AFE4400_Set_Register(4,23,2000); //ADCRSTSTCT1
      AFE4400_Set_Register(4,24,2003); //ADCRSTENDCT1
      AFE4400_Set_Register(4,25,4000); //ADCRSTSTCT2
      AFE4400_Set_Register(4,26,4003); //ADCRSTENDCT2
      AFE4400_Set_Register(4,27,6000); //ADCRSTSTCT3
      AFE4400_Set_Register(4,28,6003); //ADCRSTENDCT3

      AFE4400_Set_Register(4,29,7999); //PRPCOUNT

      AFE4400_Set_Register(4,30,0x100); //CONTROL1
      //AFE4400_Set_Register(4,31,0x004481); TIA_AMB_GAIN
      AFE4400_Set_Register(4,33,0x004141); //TIA_AMB_GAIN
      AFE4400_Set_Register(4,34,0x8F8F); //LEDCNTRL
      AFE4400_Set_Register(4,35,0x100); //CONTROL2
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

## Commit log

2018-05-09 start-up of the pcb projects
    [MonitorMain.sch]
2018-05-09 Add TI ADS1293 stuff
    [MonitorMain.sch]
2018-05-14 pcb stuff
    [ADS1293testcircuit.GBL, ADS1293testcircuit.GBO, ADS1293testcircuit.GBS, ADS1293testcircuit.GTL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]
2018-05-17 some AFE PCB Stuff
    [ADS1293+AFE4400testpcb.brd, ADS1293+AFE4400testpcb.sch, afe4400testpcb.sch]
2018-05-24 Add Arduino ADS1293 test code
2018-05-27 afe4400 pcb stuff
    [ADS1293+AFE4400testpcb.brd, ADS1293+AFE4400testpcb.sch]
2018-05-27 almost complete AFE PCB
    [ADS1293+AFE4400testpcb.brd, ADS1293+AFE4400testpcb.sch]
2018-05-29 Finishing ADS&AFE joint test pcb
    exporting gerber
    [ADS1293+AFE4400testpcb.brd, ADS1293+AFE4400testpcb.sch, copper_bottom.gbr, copper_top.gbr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]
2018-05-29 Add PCB money
2018-05-30 doing main PCB stuff
    [MainBoard.brd, MainBoard.sch, MonitorMain.sch]
2018-05-31 finishing Main PCB
    [MainBoard.brd, MainBoard.sch]
2018-05-31 main PCB finished
    [MainBoard.brd, MainBoard.sch, MainPCBParts.xlsx]
2018-06-01 finished main PCB
    [MainBoard.brd, copper_bottom.gbr, copper_top.gbr, drills.xln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]
2018-06-05 update some kind of mianPCB
    [MainBoard.brd]
2018-06-05 Revert "Merge branch 'master' of https://github.com/celelion/ECGMonitor"
    This reverts commit f7783cc06e649bc8b4ab999284b80d95ebf74241, reversing
    changes made to 6526a36a7f04e243d33003dbca553b52cb26d685.
    [MainBoard.brd]
2018-06-10 AFE Test Arduino code
2018-06-11 Fianl Complete of MainPCB
    [copper_bottom.gbr, copper_top.gbr, drills.xln, gerber_job.gbrjob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]
2018-06-11 cleaning main PCB stuff
    [copper_bottom.gbr, copper_top.gbr, drills.xln, gerber_job.gbrjob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]
2018-06-20 update PCB stuff
    [MainBoard-smt.csv]
2018-06-23 Fix STE pins out & Add state indicator LED
2018-06-24 Add EEGPPG Joint test code
2018-06-25 edit BOM
    R3->0R
    10uf capacitors->1206 package
    [MainPCBParts.xlsx]
2018-06-25 using thread to compute data & do paint stuff
2018-08-19 cleaning PCB stuff
2018-08-19 Add PowerTree Parts in readme
2018-08-19 add connectors section and signal flow sections
2018-08-20 Add a 3d print case for our main PCB
    [ECGMCase.skp, ECGMCase_Base.skp, ECGMCase_Base.stl, ECGMCase_Upper.skp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]
2018-08-20 修复AFE\ADS only 模式下波形显示问题
2018-08-21 Power Consumption Ana Data
2018-08-26 case pic

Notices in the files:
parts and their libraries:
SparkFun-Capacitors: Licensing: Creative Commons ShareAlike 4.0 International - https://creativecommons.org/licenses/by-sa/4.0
